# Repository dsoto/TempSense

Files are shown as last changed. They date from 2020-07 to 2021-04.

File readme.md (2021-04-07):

# TempSense Temperature Sensor

The first goal of the project is to provide a convenient and cost-effective logger for temperature observations in classrooms or laboratories.
The second goal of the project is to create an accessible introduction to scientific instruments and visualization through a highly-scaffolded open source hardware/software project.

This repository contains the specifications and schematics for the hardware, software to log temperatures, and potential lessons for students.

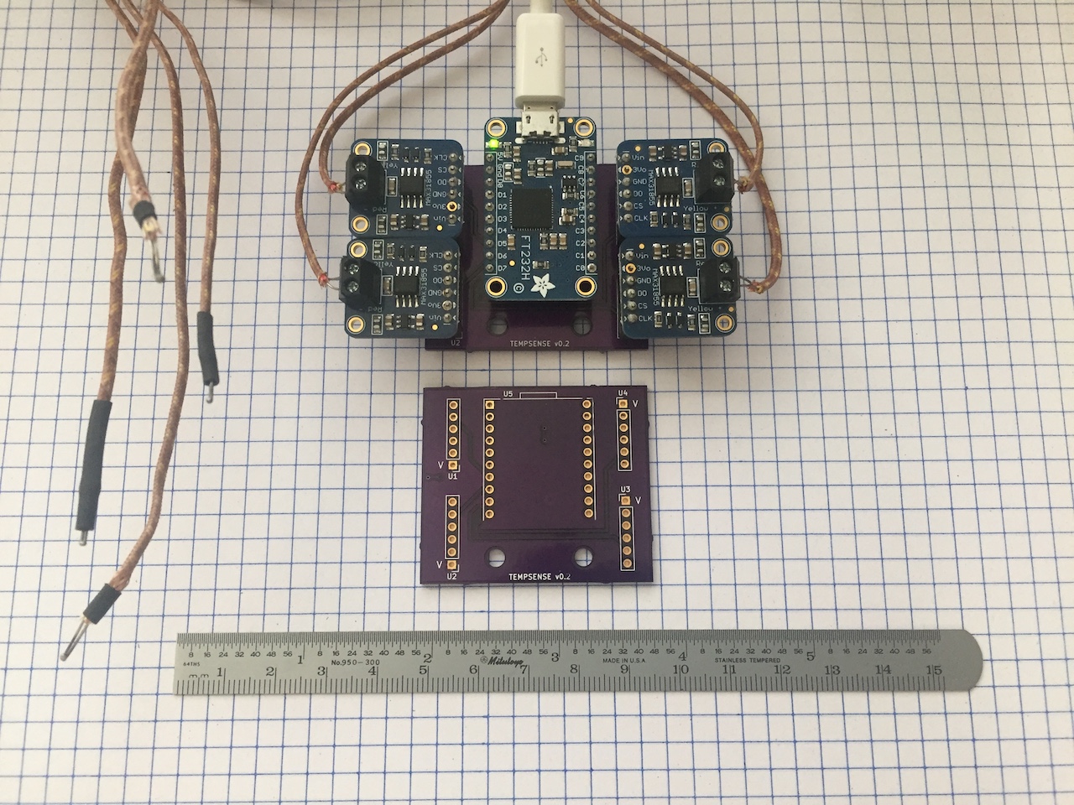
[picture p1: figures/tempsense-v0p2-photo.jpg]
PCB with USB bridge and connected sensors.


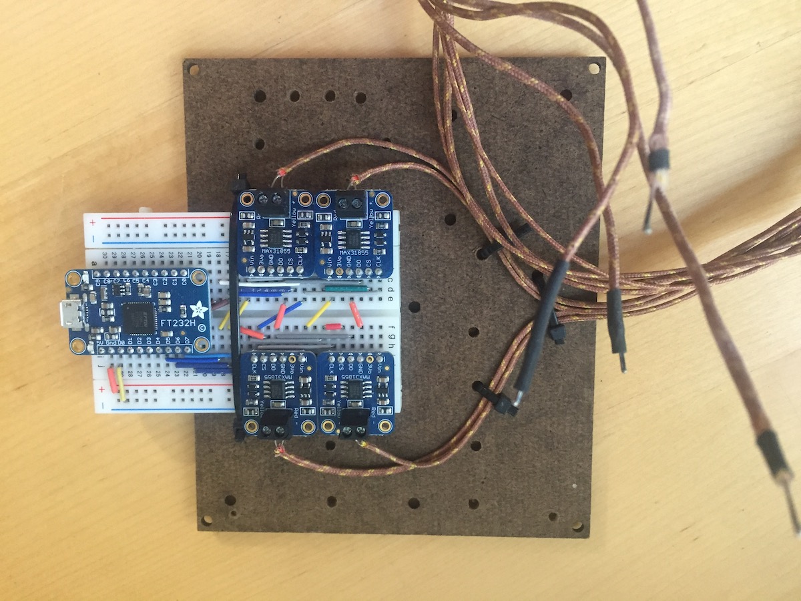
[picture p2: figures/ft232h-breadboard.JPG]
USB bridge and sensors on solderless breadboard.


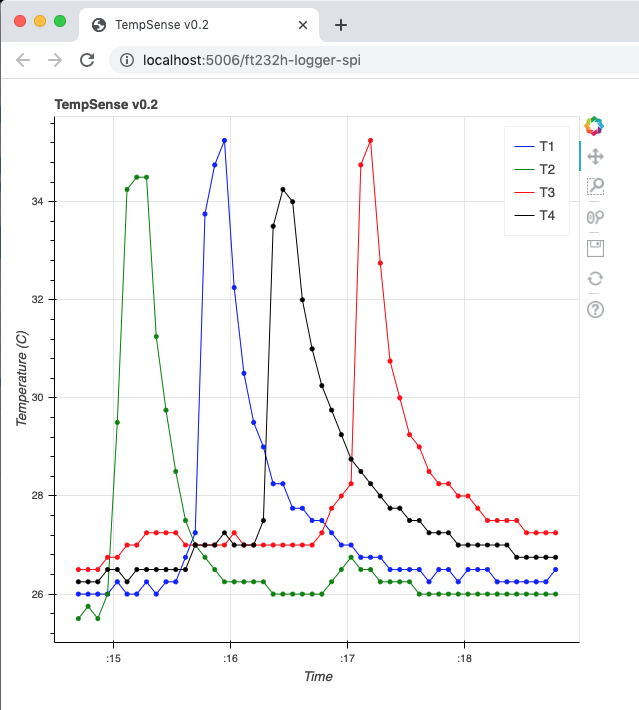
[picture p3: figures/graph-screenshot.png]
Screenshot of real-time graph output.


The hardware in this project is licensed under CERN-OHL-P v2.

The software in this project is licensed under MIT.

The documentation in this project is licensed under CC-BY 4.0.

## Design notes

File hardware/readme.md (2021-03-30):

# TempSense Temperature Logger

This is a simple multi-channel temperature logger board and real-time display application.

This folder contains the circuit schematic and board layout files in KiCad format.

# Ordering

A circuit board can be purchased at this 
[OSHPark link](https://oshpark.com/shared_projects/nJNRbfIO).

# License

This software is released under the CERN-OHL-P v2 license.



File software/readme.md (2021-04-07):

# TempSense Temperature Logger

This is a simple multi-channel temperature logger board and real-time display application.

The temperature logger uses temperature sensors with a digital interface that responds to requests for data over serial and is implemented in CircuitPython.

The real-time display uses a python streaming graphing app (Bokeh) to request temperature data from the logger board and post to a graph on a laptop or computer.

# Running

The included shell scripts export the environment variable, activate the python environment with libraries, and run the script.

# Installation

The libraries for running these scripts can be installed with the conda package manager and environment file.

> conda env create -f tempsense-environment.yml

# License

Copyright 2021 Daniel Soto

Use of this source code is governed by an MIT-style
license that can be found in the LICENSE file or at
https://opensource.org/licenses/MIT.



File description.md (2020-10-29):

# Hardware in context

Temperature measurements and time series support the efficient use of energy and efforts to combat climate change.
Scaling these efforts requires the wide use of temperature sensor technologies for buildings and industrial processes and an understanding of temperature sensor instruments and data collection.
However, my conversations with energy practitioners indicate that these instruments are underutilized and often not installed properly, making the data they collect impossible to interpret.
To address these issues, more professionals need experience in collecting temperature time series early in their training.
The instrument was developed as a demonstration tool for students preparing for energy careers to help them integrate physical observations with real-time visualizations and data collection.
This instrument is well suited for energy and building-science classroom demonstrations and laboratory use, and also to general temperature logging measurements.

Existing rugged and reliable multi-channel temperature sensors of high quality exist but have relatively high price points (300--500 USD) and are not easily extended, creating a niche for this instrument.
The Omega HH1385, a four-input thermometer with a USB interface for Microsoft Windows systems and data logging capabilities, sells for 425 USD and the Extech SDL200, a 4-channel data logger for thermocouples with data logging to an SD card, sells for 360 USD.
A set of four inexpensive thermocouples for each of these would add 40--50 USD in cost.
The Pax Instruments T400 device, a 4-channel standalone logger using thermocouples with a USB interface and open hardware and software, sold for 175 USD but was discontinued.

These price points and limited extensibility present a dual opportunity to create a low-cost temperature sensor with customization that is accessible to novices.
The hardware design decisions for this instrument support three main objectives: affordability, extensibility, and approachability.
Meeting these objectives provides a convenient and cost effective temperature logger that introduces learners to scientific instruments and visualization through an approachable open-source design.

# Hardware description

Several of the design decisions lower costs to support affordability.
The use of a host computer and USB bridge removes the need for a microcontroller and supplies power via USB eliminating a battery supply.
Since the instrument is designed for stationary monitoring situations, we include no rugged case and have minimized circuit board area to reduce cost.
The instrument uses widely available thermocouples and a thermocouple amplifier circuit board where through-hole soldering performed by the end user reduces cost.

The use of a USB bridge with a CircuitPython interface provides a highly extensible platform.
The USB bridge allows communication with the digital interface of the thermocouple amplifiers using Python commands on the host computer without the need for byte-level code.
Normally this would be done by a microcontroller in the instrument, requiring code both on the instrument and the computer for data analysis and visualization.
In contrast, this instrument requires only one script with machine instructions and any modification or extension would be to a single code base rather than two.
The CircuitPython library provides compatibility with all Python libraries allowing a rich set of graphing, communication, and internet libraries to be integrated with the instrument.
Data can be sent to a database, setpoint or max/min alarms can be sent by email or text message, and real-time visualizations can be constructed.

Several design decisions were made to allow learners to understand the operation of the device and provide opportunities to extend and customize the device.
Learners are often coding novices, and the Python language is a widely-taught and approachable language.
We write the instrument code in a style that favors clarity for learners over compactness, performance, or idioms.
Instrument code that only generates text output is provided as a minimal working example showing the use of the instrument.
We also include instrument code that provides real-time graphing that can be customized once learners understand the basic operation of the instrument.
To help students verify the signal paths of the thermocouples, the traces used to select each chip for communication are clearly visible on the front of the circuit board and the circuit schematic is relatively simple.

This instrument offers several advantages relative to existing instruments.
The BOM cost is below 150 USD, lower than the other 4-channel instruments cited above.
The Omega and Extech instruments have data logging, but don't provide a multiplatform path to stream data.
Pasco provides instruments that stream data and are extensible but these use proprietary software platforms.
Providing these benefits created some tradeoffs.
The instrument requires a host computer, has no case, and is much less portable as a result.
Setting up the device requires Python and USB library installations and an environment variable configuration on the host computer which can be bewildering to new users.

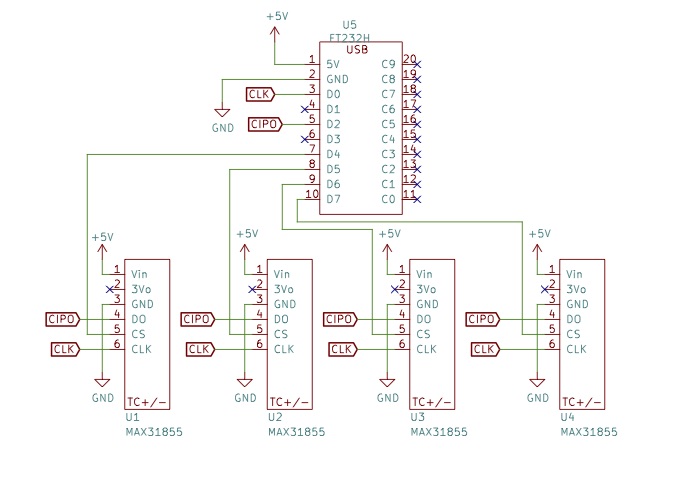
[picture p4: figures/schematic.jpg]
Schematic for printed circuit board (PCB) fabrication. Only circuit board connections are shown and the thermocouple and USB connections omitted.


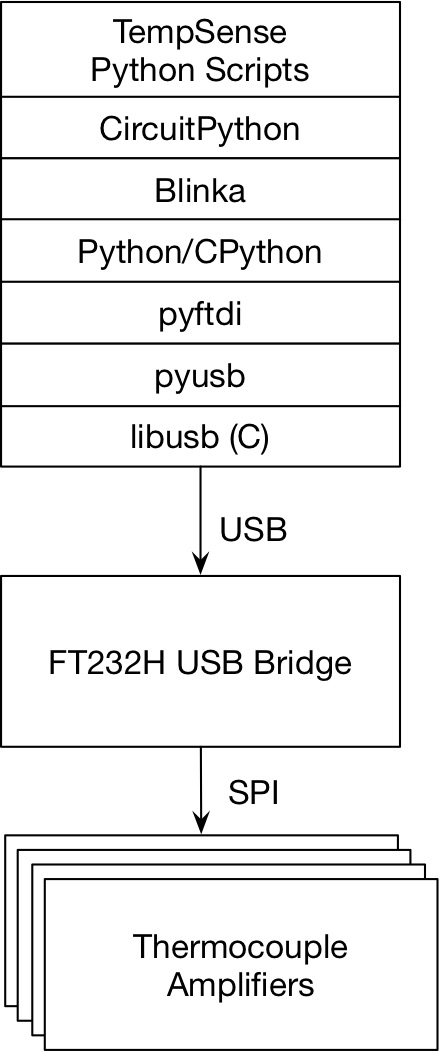
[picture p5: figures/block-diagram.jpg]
Block Diagram. The order of communication and dependencies are shown in the diagram.


Screenshot of browser-based real-time temperature graph.

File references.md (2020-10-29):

# Useful References

- [Adafruit, Welcome to Adafruit IO](https://io.adafruit.com/)
- [Adafruit, Themocouple Amplifier MAX31855 breakout board](https://www.adafruit.com/product/269)
- [Adafruit, CircuitPython Libraries on any Computer with FT232H](https://learn.adafruit.com/circuitpython-on-any-computer-with-ft232h)
- [Adafruit, CircuitPython driver for MAX31855 Thermocouple Amplifier](https://github.com/adafruit/Adafruit_CircuitPython_MAX31855)
- [Anaconda, Anaconda Individual Edition Python Distribution](https://www.anaconda.com/products/individual)
- [Anaconda, Miniconda Minimal Installer](https://docs.conda.io/en/latest/miniconda.html)
- [Bokeh, The Bokeh Visualization Library](https://bokeh.org)
- [CircuitPython, CircuitPython](https://circuitpython.org/)
- [Adafruit, CircuitPython Library Bundle Device Drivers](https://github.com/adafruit/Adafruit_CircuitPython_Bundle/tree/master/libraries/drivers)
- [Extech, SDL200: 4-Channel Datalogging Thermometer](http://www.extech.com/products/SDL200)
- [FTDI, FT232H - Hi-Speed Single Channel USB UART/FIFO IC](https://www.ftdichip.com/Products/ICs/FT232H.htm)
- [Anton Burnashev, GSpread Google Sheets Python API](https://github.com/burnash/gspread)
- [Libusb, Libusb: A cross-platform user library to access USB devices](https://libusb.info/)
- [Maxim Integrated, MAX31855 Cold-Junction Compensated Thermocouple-to-Digital Converter](https://www.maximintegrated.com/en/products/interface/sensor-interface/MAX31855.html)
- [Maxim Integrated , MAX31865 RTD-to-Digital Converter](https://www.maximintegrated.com/en/products/interface/sensor-interface/MAX31865.html)
- [Omega, 4 Input Thermometer and Data Logger with USB Interface](https://www.omega.com/en-us/sensors-and-sensing-equipment/temperature/thermometers/p/HH1384-Series)
- [Microchip, MCP2210 USB to SPI Converter with GPIO (Master Mode)](https://www.microchip.com/wwwproducts/en/MCP2210)
- [PASCO, Temperature Sensors](https://www.pasco.com/products/sensors/temperature)
- [Pax Instruments, Pax Instruments T400 Temperature Datalogger](https://www.kickstarter.com/projects/1880050573/pax-instruments-t400-temperature-datalogger)
- [OSHPark, OSHPark](https://oshpark.com/)
- [XLWings, Python for Excel](https://www.xlwings.org/)
- [Zadig, USB driver installation made easy](https://zadig.akeo.ie/)

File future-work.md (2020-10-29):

# Future Work

The combination of CircuitPython libraries and a USB bridge open several possibilities for simple instruments.
Potential upgrades to this work include extending the software for direct cloud communications, installation on small single-board computers, more flexible USB bridge models, and other sensors.

Using Python extensions, data could be logged directly to an Excel or Google spreadsheet using available open-source libraries like gspread and xlwings and sent to cloud hosting services like Adafruit IO.
Derived quantities (temperature difference, heat transfer) could also be displayed in real time by extending the code and adding graph or text outputs.
The CircuitPython and USB bridge platform could also be extended to other platforms such as single-board computers (Raspberry Pi, BeagleBone) or embedded devices (Feather, Grand Central) providing a much more portable device.

Other USB bridge devices provide features that could enable the use of more SPI devices in a future upgrade.
The FTDI FT232H USB bridge supports only two (mode 0 and 2) of the four SPI modes.
Using another USB bridge supporting all four SPI modes would allow a wider range of sensors to be used.
A USB bridge device (e.g. MCP2210) that supports all 4 SPI modes would be compatible with the MAX 31865 amplifier allowing the use of high accuracy and precision RTD sensors.

A USB bridge device that supports all 4 SPI modes (for example the MCP2210) the SPI modes (1 and 3) used by the MAX 31865 chip would allow the use of high accuracy and precision RTD sensors.
As well, the MCP2210 uses the USB Human Interface Device (HID) protocol which could simplify the driver configuration and installation process.
The FTDI FT232H and other USB bridges also support the I2C protocol expanding the list of possible sensors.
CircuitPython maintains an extensive list of libraries to interface with SPI and I2C devices.

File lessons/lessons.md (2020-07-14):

# Understand Temperature Instrument

This lesson leads a student team to shared mastery of the technical links between the multiple temperature sensors and the text or graphical output of that temperature.
Interleaved teams of students master the connections between the sensor and the output and predict which of the sensors is related to which of the outputs.
Students commit their guesses and then heat or cool invidividual temperature sensors and verify the relationships and revise their mental models.

Here is a list of distinct pairs or mappings connecting the temperature sensor to the representation of the temperature on the screen.

- between the thermocouple and the amplifier
- between the amplifier and the specific output of the USB bridge chip
- between the USB bridge chip output and the software sensor object
- between the software sensor object and the software variables
- between the software variable and the textual or graphical output 

The lesson splits a classroom of students into groups.
Each group is provided with an computer, temperature sensor board, temperature sensor software, and materials helping them understand the conceptual operation of the measurement tool.
Each of these groups are assigned one of the connections above and collaborate so that each student in the group completely understands the connection.

After each group masters a single connection, these groups are interleaved to form groups such the group has an expert for each of the connections.
These interleaved groups then trace the signal from the sensor to the output, document their understanding, and predict which thermocouple corresponds to which text or graph element.
These predictions are then tested by heating or cooling the thermocouple and observing the change in the output on the screen.
If predictions are incorrect, students have an opportunity do discover which of their assumptions were incorrect.

# Apply Instrument to Classroom Demonstration

Students collaborate and decide on the colors, shapes, and sizes of graph objects to represent the particular science lesson they are observing with the instrument.

- Students identify physical thing to monitor that is relevant to the science demonstration.
- Students decide best data representation of the (up to) four sensors for this physical situation.
- Students verify, collect, and interpret data as a team.

# Given a Problem, Imagine an Instrument 

Students identify a large issue where temperature is important to equity and human well-being.

- Influenza-like illness
- Climate change
- Heat island effect

Students design hypothesis, experiment, and data collection that could help decision, understanding, or policy.

- Students identify physical thing to monitor and how sensors represent that.
- Students identify chain how data representation moves from sensor to data storage to representation.
- Students identify data representation that best supports insight and decision making.

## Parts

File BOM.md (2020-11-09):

# Bill of materials

| Designator | Component | Number | Cost per unit (USD) | Total cost (USD) | Source of materials |
|-|-|-|-|-|-|
| | Printed Circuit board from OSHPark| 3 | 4.93 | 14.80 | OSHPark | Inorganic/Metal |
| U5 | Adafruit FT232H board | 1 | 14.95 | 14.95 | Digikey Part 1528-1449-ND | Semiconductor |
| U1--U4 | Adafruit MAX 31855 board | 4 | 14.95 | 59.80 | Digikey Part 1528-1000-ND | Semiconductor |
| U1--U4 | Type-K unshielded thermocouple | 4 | 9.95 | 39.80 | Digikey Part 1286-1099-ND | Metal |
| U1--U4 | Type-K shielded thermocouple | 4 | 5.72 | 22.88 | Digikey Part 1778-COM1706-ND | Metal |
| U1--U4 | 0.1 inch 6-pin Sockets Sullins PPPC061LFBN-RC | 4 | 0.53 | 2.12 | Digikey Part S7039-ND | Polymer/Metal |
| U5 | 0.1 inch 10-pin Sockets Sullins PPPC101LFBN-RC | 2 | 0.68 | 1.36 | Digikey Part S7043-ND | Polymer/Metal |

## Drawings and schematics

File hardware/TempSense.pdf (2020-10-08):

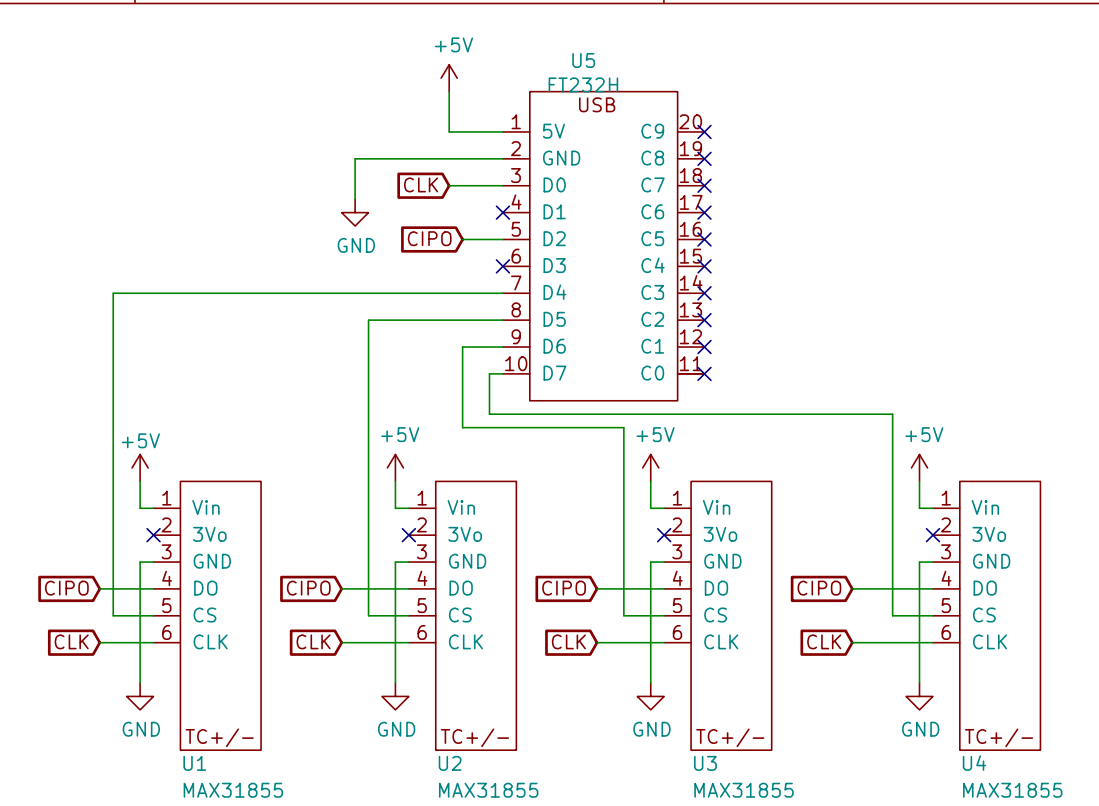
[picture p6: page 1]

File: TEMPSENSE.sch Sheet: /
Id: 1/1 Title: TEMPSENSE v0.2

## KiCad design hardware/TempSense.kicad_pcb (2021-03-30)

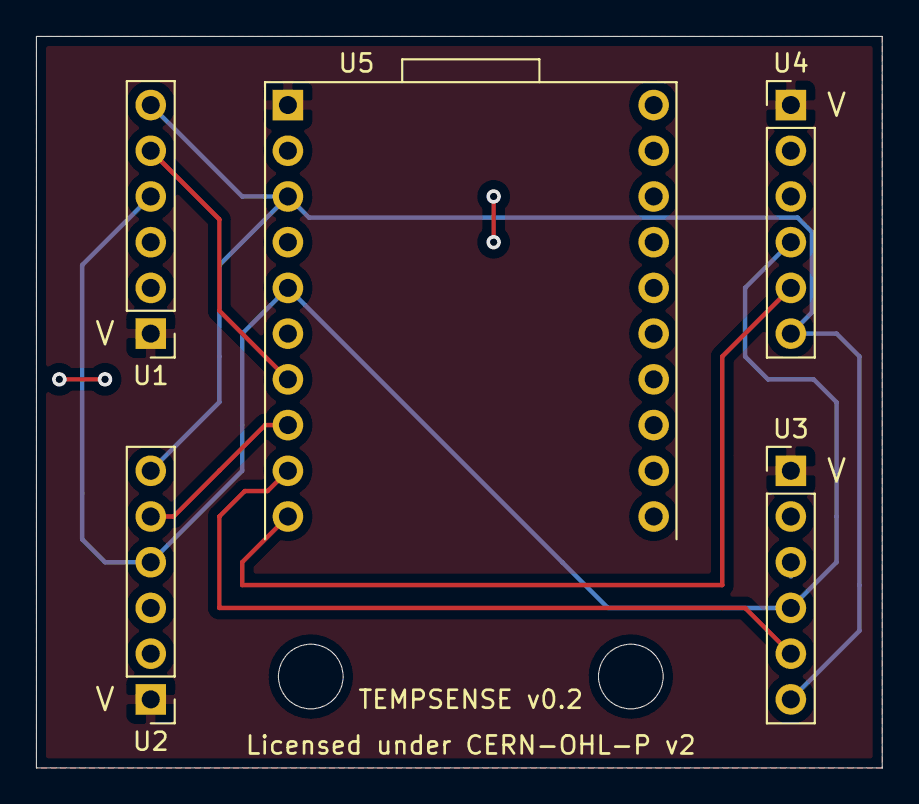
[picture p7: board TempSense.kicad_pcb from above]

Board: 2 copper layers, 47.0 x 40.6 mm, 5 parts (0 on the bottom side), 8 nets.

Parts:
U1, U2, U3, U4: MAX31855; Max-31855-board
U5: FT232H; FT232H-socket

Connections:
+5V: U1.1, U2.1, U3.1, U4.1, U5.1
CIPO: U1.4, U2.4, U3.4, U4.4, U5.5
CLK: U1.6, U2.6, U3.6, U4.6, U5.3
GND: U1.3, U2.3, U3.3, U4.3, U5.2
unnamed: U1.5, U5.7
unnamed: U2.5, U5.8
unnamed: U3.5, U5.9
unnamed: U4.5, U5.10

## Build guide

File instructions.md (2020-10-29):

# Build instructions

## Hardware

When you place your order for the bill of materials, decide if you want unshielded or shielded thermocouples or both. Shielded thermocouples are best for measurements of liquids.
You can order the PCB through OSHPark by uploading the `TempSense.kicad_pcb` file and specifying a 2-layer PCB board.
Alternately, the circuit can be built on a solderless breadboard since the number of connections is tractable.
Once you have received the PCB, you can begin the required soldering of the pins and pin receptacles to the custom PCB and the amplifier circuit boards.
Before assembly, take the usual safety measures for soldering including caution around hot objects, adequate ventilation from flux fumes, eye protection from flux or solder spatter, and low-toxicity lead-free solder.

Start by assembling the USB bridge board and the thermocouple amplifiers.
Solder the two 10-pin header strips included with the part to the FT232H USB bridge board.
For all pins and receptacles, start by soldering one pin and then verify that the pin strip is perpendicular to the PCB before continuing.
Solder the 6-pin header strip to each of your thermocouple amplifier boards.
Solder the terminal blocks to each of the thermocouple amplifier boards.
Verify the wires will enter from the outside of the board before soldering.

Next, solder the receptacles on to the custom PCB and insert the components.
Solder the two 10-pin socket strips to the circuit board to create the USB bridge connection in the U5 area.
Solder a 6-pin socket strip to the printed circuit board in the U1--U4 areas.
Insert the USB bridge in the U5 position and be sure the USB port is facing the small rectangle near the U5 text.

The orientations of the circuit boards are shown in the photo.
Insert the thermocouple amplifiers into the U1--U4 sockets.
With the thermocouple amplifiers inserted, you can attach the thermocouples.
Note the designations for thermocouple polarities on the thermocouple amplifier board.
Note that not all thermocouples follow the color convention and that a reversed thermocouple will give a lower reading with higher temperatures.

Assembled instrument and bare printed circuit board.

## Software environment

The instrument requires the installation of several software libraries that translate the Python commands in the scripts to the digital signals to read temperatures from the thermocouple amplifiers.
We first install the TempSense library containing the scripts for reading and recording temperatures.
The linked Mendeley Data repository contains these scripts. Place the software folder in a convenient location on your hard drive.

Next we install the libraries to translate the Python scripts to commands for the USB bridge and thermocouple amplifiers.
We start with a Python/CPython installation for your host computer.
Many computers include Python/CPython, but it is useful to install a Python implementation that allows the creation of custom environments with installed libraries that can be activated or deactivated.
An excellent option for installing Python with these environments is the Anaconda Individual Python distribution or the Miniconda distribution.
Anaconda is a multi-gigabyte distribution containing many libraries for scientific computation while the Miniconda distribution is a minimal distribution that can be expanded.
These distributions provide the Python language and also an installer (conda) that we use to install other Python software in custom environments.
Navigate to the websites for these installations and follow the instructions for your host computer operating system.
With the Python software installed, you can proceed to the creation of the custom software environment for the tool.

The Mendeley Data repository contains the file, `tempsense-environment.yml`.
When run, this file downloads and installs the necessary libraries between the Python scripts and USB bridge and places them in an environment named tempsense.
Navigate to the directory containing the file in the command line and execute the following command.

    > conda env create -f tempsense-environment.yml

At this point the libraries are installed and we move on to the verification of their installation and the links between them.

We start by verifying the presence of our custom python environment, tempsense.
Activate the tempsense environment and view the installed libraries by typing the following commands.
Note that some systems may use `source activate tempsense` or `activate tempsense` instead.

    > conda activate tempsense
    > conda list

If you see a listing of several packages, Python/CPython and the custom environment have been installed correctly.

To verify that the Python and C USB libraries (pyusb and libusb) are correctly configured and can connect to the USB bridge, activate the tempsense environment and open a Python interpreter by typing python at the command line, then plug in the TempSense device to the host computer and type the following.

    >>> import usb
    >>> import usb.util
    >>> dev = usb.core.find(idVendor=0x0403, idProduct=0x6014)
    >>> print(dev)

If you see a text table describing the device without errors, this is configured correctly.

To verify that the Python library to communicate with the FTDI bridge over USB is correctly configured type the following in a Python interpreter with the tempsense environment activated.

    >>> import pyftdi.ftdi
    >>> pyftdi.ftdi.Ftdi.list_devices()

You should see a listing for the connected FTDI USB bridge device verifying that the pyftdi library is installed.

If you have problems, the most common issues involve the C USB drivers.
On Windows, Zadig is a free tool for associating a driver with the USB bridge.
You may need to manually install the C USB library, libusb by visiting the website and downloading.
More extensive troubleshooting and detailed instructions for OS X, Linux, and Windows can be found in the FT232H tutorial on the Adafruit site.

In the last step of the installation and configuration we create an environment variable to instruct the CircuitPython library of the type of hardware (the USB bridge) it will be sending instructions to.
If you are comfortable setting environment variables, you can include it in a start-up script for your computer.
Otherwise, we set the environment variable before each use of the instrument by typing the following in the comand line.
Note some machines use a different command than export (Some Windows shells use set).

    > export FT232H_Blinka=1

To ensure that the CircuitPython library, Blinka compatibility layer, and environment variable are correctly configured type the following in a python interpreter with the tempsense environment activated and the device plugged in.

    >>> import board

If this runs without an error, the CircuitPython libraries are connected and you are ready to run the instrument.

# Operation instructions

To operate the instrument, we configure the Python scripts with our time intervals or other customizations, decide on text or graph output, and run the shell script to set the environment variable and run the appropriate Python script.
Open the script in a text editor and set the measurement interval in the Python scripts to set the time interval between samples and comment out any code to read or display any sensors you aren't using.
You can also set the variable for the location of any log files you generate.

Place the sensors in the desired locations while using caution when placing probes on hot surfaces or in hot areas.
Next we choose the text output program or the graphing program and launch the appropriate shell script.
These launch scripts activate the tempsense environment, set the environment variable for the USB bridge, and run the Python commands script.
In both cases, the same commands activate the custom python environment and set the environment variable as in the installation and testing.
For the text script, we run with a python command `python tempsense-text.py`.
For the graph script, we run with a bokeh command `bokeh serve --show tempsense-graph.py`.
These three commands are placed in script files for convenience.
The files are written for UNIX-like systems and may need to be revised for other operating systems.

Run the launch script for text output by typing

    > sh launch-text.sh

You should see a text listing of time stamps and temperature
observations output to the console.

To run the real-time graphing application, run the launch script by typing

    > sh launch-graph.sh

You should see a browser window open with a graph window.
To end the programs, type Ctrl-C in the console window to interrupt the program.

Graphing in Browser Window

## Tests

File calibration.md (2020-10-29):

# Calibration

We validated and characterized the instrument using water ice-point and boiling-point calibrations with a single sensor.

An ice-point calibration was performed with an ice-water mixture in a 500 ml beaker.
During the ice-point calibration 100 data points were taken at 5 second intervals with a shielded thermocouple.
The thermocouple was placed near the top of the container where both ice and water were present.
The observed mean over the 100 samples was from 2.52 degrees celsius and the standard deviation was 0.072 degrees Celsius.

A boiling point calibration was performed with 500 ml of boiling water on a laboratory hot plate.
During the boiling-point calibration, 100 data points were taken at 1 second intervals with a shielded thermocouple.
The mean reading was 98.7 degrees with a standard deviation of 0.15 degrees Celsius.

These means are consistent with a typical thermocouple accuracy of 2.2 C and the deviations are consistent with the MAX 31855 amplifier resolution of 0.25 C.
For users wanting higher control over calibration, the cold-junction compensation code can be accessed in the MAX31855 CircuitPython library.

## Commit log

2020-07-15 adds file that calls a single sensor and prints to screen
2020-07-16 adds code with four sensor readings
2020-08-24 adds circuit files
    [TEMPSENSE.kicad_pcb, TEMPSENSE.sch]
2020-09-21 updates schematic and pcb
    [TEMPSENSE.kicad_pcb, TEMPSENSE.sch]
2020-10-08 changes filenames to camel case
    [TempSense.kicad_pcb, TempSense.sch]
2020-10-29 adds calibration and future work sections
2020-11-09 adds bill of materials
2021-03-30 adds license information to files
    [TempSense.kicad_pcb, TempSense.sch]
2021-04-07 change folder name to hardware
    [TempSense.kicad_pcb, TempSense.sch]
